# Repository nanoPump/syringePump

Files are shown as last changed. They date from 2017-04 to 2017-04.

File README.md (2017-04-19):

# Syringe Pump
This repository contains the design files and software for an open-source syringe pump

## DIY Bill of Materials
1. Mechanical Parts
    1. 3x 400by500mm 4.5mm thick Acrylic Sheets - [Recomended Supplier](http://uk.rs-online.com/web/p/solid-plastic-sheets/0824525/) in the UK or worldwide using Part Number for [RS Components](http://rs-online.com): 824-525
    2. SFU1605 250mm Ballscrew with corresponding BF12 and BK12 Support bearings. These can easily be found on ebay.
    3. LM8UU Linear Ball Bearings - 8mm Shaft
    4. 2x 8mm Stainless Steel Rods 230mm Drilled and Tapped M3
    5. Shaft coupler 8mm to 10mm
    
2. Electrical Parts
    1. 12V Power Supply
    2. Stepper Motor driver: TB6600 or similar
    4. Stepper Motor - Nema 17 - 100:1 Planetary Gearbox: 17HS19-1684S-PG100
        * Different Stepper Motors or different gearbox ratios could be used. However adjustments would have to be made to the entire system
    5. Arduino Uno
    6. USB Cable

## Design and DIY Guidelines
###### Laser Cutting the Linear Stage for the Syringe Pump
The file `Syringe_Pump__Master_12_4_17_LASER_CUT_4.5mm_acrylic.AI` contains the Adobe Illustrator design for laser cutting 3 pieces of **400by500mm** 4.5mm (5mm) thick Acrylic/Plexiglass which can then be used to build the remaining mechanical parts of the syringe pump

###### Electrical Connections

Pin Correspondence for the electrical connections:
```
Power Supply     TB6600 Stepper Driver
+12V             DC/Power (+)
0V               DC/Power (-)
```
```
Stepper Motor Coil      TB6600 Stepper Driver
Red Wire                A(+)
Blue Wire               A(-)
Green Wire              B(+)
Black Wire              B(-)
```
```
Arduino     TB6600 Stepper Driver
Vin         DC/Power (+)
Pin 2       Enable
Pin 3       Step
Pin 4       Direction
Ground      Enable (-), Step (-), Direction (-), DC/Power (-)
```

###### 

## Arduino | Control Board Software Installation
Open the Arduino sketch file named `SP_1_3v2.ino` using the Arduino IDE and upload to the Arduino. A typical application scenario shouldn't require any modifications to the code.

## Installing the GUI
###### Windows
1. Install Python (32/64Bit depending on your system)
   * You can get the latest version from [here](https://www.python.org/downloads/windows/)
   * Make sure `pip` is also included in the binary installers - This should be the default since version 3.4
2. Install `pyserial` using `pip`
```
sudo pip install pyserial
```
3. Install `PyQt5` using `pip`
```
sudo pip install PyQt5
```
4. Navigate to this repository and run
```
pyuic5 mainwindow.ui>mainwindow_auto.py
python pump_control.py
```

###### Linux
1. Install Python (current latest version is 3.6)
```
sudo apt-get install python3.6
```

2. Install `pyserial` using `pip`
```
sudo pip install pyserial
```
3. Install `PyQt5` using `pip`
```
sudo pip install PyQt5
```
4. Navigate to this repository and run
```
pyuic5 mainwindow.ui>mainwindow_auto.py
python pump_control.py
```

###### MacOS
1. Install Python (current latest version is 3.6)
    * You are going to need a package installer like [Homebrew](https://brew.sh) - Follow the instructions if you don not have it
    * One you have installed `Homebrew` you can run it to install python. This should install pip3 (pip for the python3 homebrew package) - Its called pip3 to avoid issues with python2.7
  ```
  brew install python3
  ```
    
2. Install `pyserial` using `pip`
```
sudo pip3 install pyserial
```
3. Install `PyQt5` using `pip`
```
sudo pip3 install PyQt5
```
4. Navigate to this repository and run
```
pyuic5 mainwindow.ui>mainwindow_auto.py
python3 pump_control.py
```

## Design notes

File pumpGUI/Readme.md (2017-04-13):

# Cross-platform Pump GUI
After having installed the appropriate dependencies, run:
```
pyuic5 mainwindow.ui>mainwindow_auto.py
python pump_control.py
```

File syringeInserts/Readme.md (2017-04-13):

# Syringe Inserts
Files for the syringe inserts can be found on [Thingiverse](http://thingiverse.com)

## VWR 5ml Gastight Syringe

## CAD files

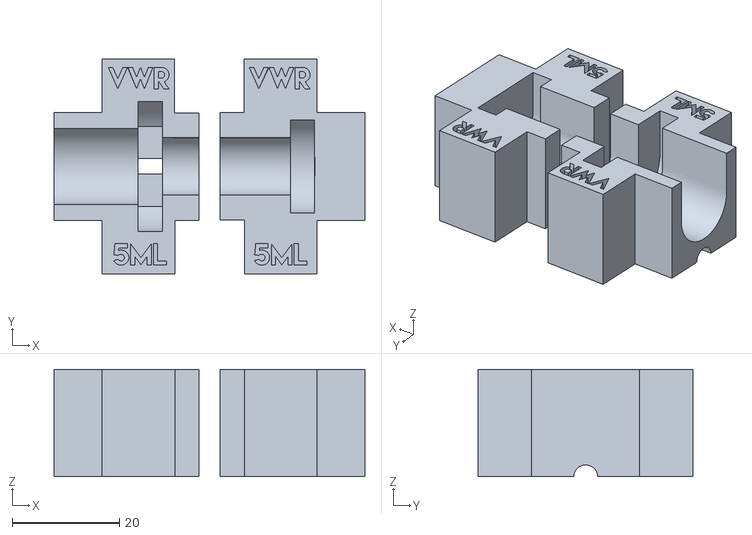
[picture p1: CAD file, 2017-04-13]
syringeInserts/VWR 5ml 3D printed Syringe Pump Insert 13_4_17.stl
57.9 x 40.1 x 20.0

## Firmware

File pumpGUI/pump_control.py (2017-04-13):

# always seem to need this
import sys
import math
import serial
import time
import glob

# This gets the Qt stuff
import PyQt5
from PyQt5.QtWidgets import *

# This is our window from QtCreator
import mainwindow_auto

# create class for our GUI
class MainWindow(QMainWindow, mainwindow_auto.Ui_MainWindow):
    global screw_draw
    screw_draw = 5
    global steps
    steps = 200
    global gearing
    gearing = 100
    global stop
    stop = "s"
    stop = stop.encode()
    
    global min_freq
    min_freq = 31
    global max_freq
    max_freq = 970
    global ser1
    global out1
    
#   Define signals to be sent for fast empty/fill
    global fast_fill
    global fast_empty
    fast_fill = str(2) + " 0" + str(max_freq) + " " + str(9999) + " " + str(999)
    fast_fill = fast_fill.encode()
    fast_empty = str(1) + " 0" + str(max_freq) + " " + str(9999) + " " + str(999)
    fast_empty = fast_empty.encode()
    
    def serial_port_scan(self):
#       clear existing elements in comboBox
        self.serial_port.clear()
        if sys.platform.startswith('win'):
            ports = ['COM%s' % (i + 1) for i in range(256)]
        elif sys.platform.startswith('linux') or sys.platform.startswith('cygwin'):
            # this excludes your current terminal "/dev/tty"
            ports = glob.glob('/dev/tty[A-Za-z]*')
        elif sys.platform.startswith('darwin'):
            ports = glob.glob('/dev/tty.*')
        else:
            raise EnvironmentError('Unsupported platform')
    
        result = []
        for port in ports:
            try:
                s = serial.Serial(port)
                s.close()
                result.append(port)
            except (OSError, serial.SerialException):
                pass
#        Loop through array of port strings and add them to comboBox
        for port in result:
            self.serial_port.addItem(port)
        
        self.OK_btn.setEnabled(1)
        print(result)

    
    def pressedOKButton(self):
#            global ser1
#            serialPort = self.serial_port.currentText()
#        
#            ser1 = serial.Serial(serialPort,
#                                baudrate=9600,
#                                bytesize=serial.EIGHTBITS,
#                                parity=serial.PARITY_NONE,
#                                stopbits=serial.STOPBITS_ONE,
#                                timeout=1,
#                                xonxoff=0,
#                                rtscts=0
#                                )
#        
#            ser1.setDTR(False)
#            time.sleep(1)
#            ser1.flushInput()
#            ser1.flushOutput()
#            ser1.setDTR(True)
            self.syringe_btn.setEnabled(0)
            self.rate_btn.setEnabled(0)
            self.target_btn.setEnabled(0)
            self.run_btn.setEnabled(0)
            self.checkBox.setCheckable(0)
            self.stackedWidget.setCurrentIndex(0)


#    ser1 = serial.Serial('/dev/tty.usbmodemFA131',
#                         baudrate=9600,
#                         bytesize=serial.EIGHTBITS,
#                         parity=serial.PARITY_NONE,
#                         stopbits=serial.STOPBITS_ONE,
#                         timeout=1,
#                         xonxoff=0,
#                         rtscts=0
#                         )
#    # Serial port 2 to control ethanol syringe
#    ser2 = serial.Serial('/dev/tty.usbmodemFD121',
#                        baudrate=9600,
#                        bytesize=serial.EIGHTBITS,
#                        parity=serial.PARITY_NONE,
#                        stopbits=serial.STOPBITS_ONE,
#                        timeout=1,
#                        xonxoff=0,
#                        rtscts=0
#                        )
#                         
#    ser1.setDTR(False)
#    time.sleep(1)
#    ser1.flushInput()
#    ser1.flushOutput()
#    ser1.setDTR(True)
#    
#    ser2.setDTR(False)
#    time.sleep(1)
#    ser2.flushInput()
#    ser2.flushOutput()
#    ser2.setDTR(True)

    def encodePumpInstructions(self, dir, freq, secs, millis):
        dir = str(dir)
        freq = str(freq)
        secs = str(secs)
        millis = str(millis)
        
        if len(freq) == 1:
            freq = "000"+freq
        elif len(freq) ==2:
            freq = "00" + freq
        elif len(freq) == 3:
            freq = "0" + freq
        else:
            freq = freq
        
        if len(secs) == 1:
            secs = "000"+secs
        elif len(secs) ==2:
            secs = "00" + secs
        elif len(secs) == 3:
            secs = "0" + secs
        else:
            secs = secs
        
        if len(millis) == 1:
            millis = "00"+millis
        elif len(millis) ==2:
            millis = "0" + millis
        else:
            millis = millis
        
        out = dir + " " + freq + " " + secs + " " + millis
        out = out.encode()
        print(out)
        return out
    
    # Writes instructions to serial port.
    def serWrite(self, out):
        ser1.write(out)

    def sendStopInstructions(self):
        ser1.write(stop)
        ser1.close()
        ser1.open()


    def pressedModeButton(self):
#       When Mode button pressed, uncheck checkbox, clear subsequent display fields, and set all subsequent buttons to unclickable (except syringe button)
        self.checkBox.setChecked(0)
        self.rate_btn.setEnabled(0)
        self.target_btn.setEnabled(0)
        self.run_btn.setEnabled(0)
        self.checkBox.setCheckable(0)
        self.syringe_table.setItem(0,0,QTableWidgetItem(str(' ')))
        self.rate_table.setItem(0,0,QTableWidgetItem(str(' ')))
        self.target_table_time.setItem(0,0,QTableWidgetItem(str(' ')))
        self.target_table_vol.setItem(0,0,QTableWidgetItem(str(' ')))
        
#        Change to 'Mode' page
        self.stackedWidget.setCurrentIndex(1)

    def pressedSyringeButton(self):
#        When Syringe button pressed, uncheck checkbox, clear subsequent display fields, set all subsequent buttons to unclickable (except rate button)
        self.checkBox.setChecked(0)
        self.target_btn.setEnabled(0)
        self.run_btn.setEnabled(0)
        self.checkBox.setCheckable(0)
        self.rate_table.setItem(0,0,QTableWidgetItem(str(' ')))
        self.target_table_time.setItem(0,0,QTableWidgetItem(str(' ')))
        self.target_table_vol.setItem(0,0,QTableWidgetItem(str(' ')))
        
#        Change to 'Syringe' page
        self.stackedWidget.setCurrentIndex(2)
    
    def pressedRateButton(self):
#        When rate button pressed, uncheck checkbox, clear target display field, make checkbox & run button unclickable
        self.checkBox.setChecked(0)
        self.run_btn.setEnabled(0)
        self.checkBox.setCheckable(0)
        
        self.target_table_time.setItem(0,0,QTableWidgetItem(str(' ')))
        self.target_table_vol.setItem(0,0,QTableWidgetItem(str(' ')))

#       Depending on which rate units selected, min/max rates are adjusted
        global adjust
        global units
        global time_units
        
        if self.comboBox_3.currentIndex()==0:
            adjust = 1
            units = ' ul/sec'
            time_units = ' secs'
        elif self.comboBox_3.currentIndex()==1:
            adjust = 60
            units = ' ul/min'
            time_units = ' mins'
        elif self.comboBox_3.currentIndex()==2:
            adjust = 1/1000
            units = ' ml/sec'
            time_units = ' secs'
        elif self.comboBox_3.currentIndex()==3:
            adjust = 60/1000
            units = ' ml/min'
            time_units = ' mins'

#       Display min/max rates and step resolution
        self.maxrate_table.setItem(0,0,QTableWidgetItem(str(round(max_rate_uls*adjust,2))+ units))
        self.minrate_table.setItem(0,0,QTableWidgetItem(str(round(min_rate_uls*adjust,2))+ units))
        self.stepres_table.setItem(0,0,QTableWidgetItem(str(round(min_rate_uls/min_freq,3))+ ' ul/step'))
        self.units_table.setItem(0,0,QTableWidgetItem(units))

#       Change to 'Rates' page
        self.stackedWidget.setCurrentIndex(3)
    
    def pressedTargetButton(self):
#        Unchecks and sets checkbox to unclickable
        self.checkBox.setCheckable(0)
        self.checkBox.setChecked(0)
        self.stackedWidget.setCurrentIndex(4)
    
    def pressedRunButton(self):
#        Re-enable Stop button in case of stop/restart
        self.stop_btn.setEnabled(1)
        
        global microstepping
        microstepping = 1
        
#        Redundant checkBox verification
        if self.checkBox.isChecked()==1:
#            Checks if target is volume or time, converts to volume
            if self.radioButton.isChecked()==1:
                volume = target_ul
            else:
                volume = rate_uls*target_sec
            
#            Performs calculations for frequency with microstepping off
            steps_rev = steps*gearing*microstepping
            vol_rev = plunger_area*screw_draw
            vol_step = vol_rev/steps_rev
            min_volsec = vol_step*min_freq
            
#            If calculated rate is below min rate, turn microstepping on
#            Use while loop to increase microstepping until condition satisfied?
            if min_volsec>rate_uls:
                microstepping = 8
            else:
                microstepping = 1
            
#            Re-perform calculations with new microstepping value to calculate drive freq
            steps_rev = steps*gearing*microstepping
            vol_rev = plunger_area*screw_draw
            vol_step = vol_rev/steps_rev
            freq = round(rate_uls/vol_step)
            
#            Calculate pump time and split into secs/millis
            pump_time = volume/rate_uls
            pump_time_secs = math.floor(pump_time)
            pump_time_millis = (pump_time-pump_time_secs)*1000
            
#           Changes time display to minutes if larger than 60 secs, possible problem with 'time_units', 'adjust' and 'units' being declared as global in both 'RateChanged' function and 'RatePressed' function
            if time_units == ' mins':
                pump_time = pump_time/60

            
#            Print results to Terminal for verification purposes
            print(freq)
            print(pump_time)
            print(mode)
            print(microstepping)
            
#            out = self.encodePumpInstructions(mode,freq,pump_time_secs,pump_time_millis)
#            serWrite(out)

#            Create display parameters for 'Progress' page
            if mode == 1:
                mode_str = 'Pumping'
            elif mode == 2:
                mode_str = 'Filling'
            
#            Display parameters on 'Progress' page
            self.display_mode_table.setItem(0,0,QTableWidgetItem(mode_str))
#            For some reason this is not converting to selected rate units, always stays at ul/s and secs
            self.display_rate_table.setItem(0,0,QTableWidgetItem(str(round(rate_uls*adjust,2))+ units))
            self.display_time_table.setItem(0,0,QTableWidgetItem(str(round(pump_time,2))+time_units))
            print(rate_uls)
            print(adjust)
            print(units)
#           Sets page to 'Progress' page
            self.stackedWidget.setCurrentIndex(5)
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
